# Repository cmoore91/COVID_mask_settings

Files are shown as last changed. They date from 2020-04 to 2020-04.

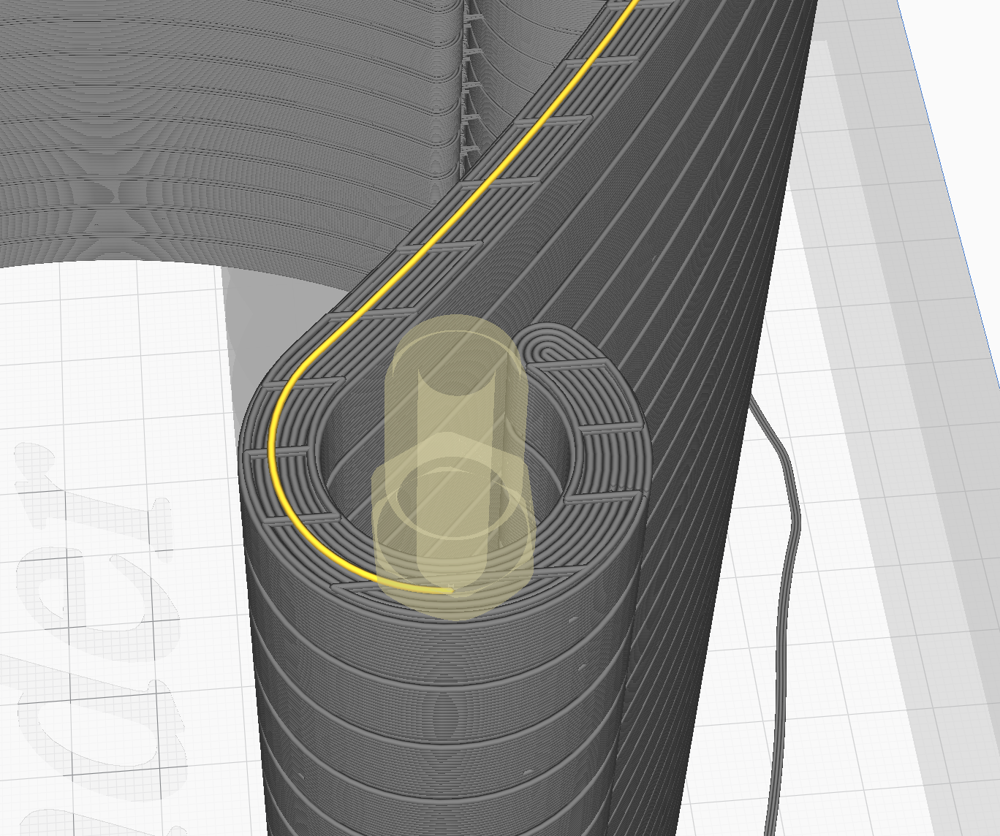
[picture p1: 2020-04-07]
inside_walls_first.png

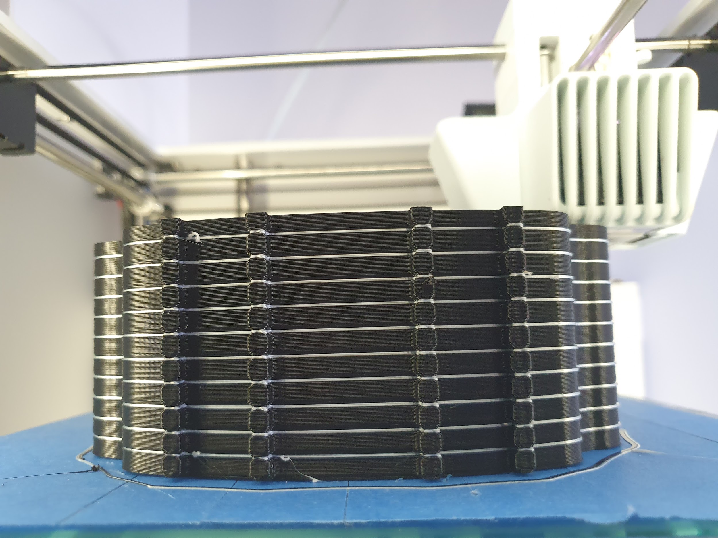
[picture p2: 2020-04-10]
protective-visor-by-3dverkstan/breakaway_stack3.jpg

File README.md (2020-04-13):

# COVID mask settings
### 3D print settings I have optimized for mass production of the 3DVerkstan faceshield on an Ender 3 Pro.  
### Disclaimer: This is intended to assist Chapman University affiliated personnel for charity purposes, and I am not liable for your printer imploding  

* Printer: Creality Ender 3 Pro with OctoPi and BLtouch self-leveling bed 0.4mm nozzle
* Slicer: Ultimaker Cura 4.5.0
* CAD Software: Autodesk Fusion360
* Filament: Matterhackers PRO PLA

In this repository, I have attached the STL and cura profile I used if you want to tweak the settings.  I have 2 versions: 
* fast and loose: decent quality for rapid speed.  some unsupported areas are a little rough
* slow and smooth: I recommend this one.  at 0.3mm layer height you can get it almost as fast as above.  

I also have 2 open source droplet containment box designs.
* the first one is mine: https://a360.co/2RrGePB  
* the second one is in the Flatpackv5 folder (from https://www.aerosolblock.org/)

Otherwise find the
plug-and-play g-code file here: https://drive.google.com/a/chapman.edu/file/d/1QBju7udUCOP3C-gHDJ0qYh54JztkdXBj/view?usp=sharing
* Note: if you dont have self-leveling, you need to remove the relevant g-code from the preamble in a text editor.

This can accomplish printing 35 Shield Frames in <30 hours, or 50 minutes per shield.  

The frames are easily cracked apart with a paint scraper, razor blade or metal spatula.  I recommend cracking apart the tips of the arms first.  

For people not using Cura slicer and want to copy the settings I used, but warning: mileage may vary.  

The **CRITICAL** slicer settings are as follows:
* Orientation: 90 degrees rotation from default (so mirror plane of the frame is parallel to x-axis) (yes this matters)
* Layer Height: 0.28 mm
* Wall Line Count: 5 
* Top Layers: 3
* Outer Before Inner Wall: NOOOOO
* Filter Out Tiny Gaps: Yes
* Fill Gaps Between Walls: No
* Infill Density: 5%
* Infill Pattern: Gyroid
* Connect Infill Lines: Yes
* Min Infill Area: 4 mm^2
* Print Temp: 210 C
* Build Plate Temp: 60 C
* Speed: 60 mm/s
* Support Placement: Everywhere
* Support Wall Line Count: 0
* Support Density: 10%
* Min Support Area: 10mm^2
* Build Plate Adhesion: Skirt
* IT IS VERY IMPORTANT YOU SET THE WALLS TO START FROM THE INSIDE FIRST AND MOVE OUTWARDS TO TAKE ADVANTAGE OF THE VERY SPARSE SUPPORTS

Here is the original design.  Make sure to use North American Version 
https://3dverkstan.se/protective-visor/protective-visor-versions/

contact me at c.stephen.moore@gmail.com with any feedback or questions

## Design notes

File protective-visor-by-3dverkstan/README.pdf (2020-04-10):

# Protective Visor by 3DVerkstan

### By: (erikcederb) License: Commercial use is allowed, you must attribute the creator, you may remix this

work and the remixed work should be made available under this license.

### Published on: Apr 03, 2020 Located at: http://www.youmagine.com/designs/protective-visor-by-3dverkstan Short description:

Protective visor optimized for fast FDM printing

### Description:

I would like to thank our fantastic team at 3DVerkstan who all have contributed massively! Since the medical community currently (2020-03-20) has a urgent need for protective visors and other PPE for our heroes that spends their days battling COVID-19, myself and my co-workers at 3DVerkstan have spent a lot of time during the past few days designing a printable visor. This in a WORK IN PROGRESS, and might get multiple revisions during the coming days/weeks, but this first released version is the first one on its way to be tried out by a local hospital. The plastic shield can be made out of any semi-stiff plastic sheet between 0.1 and 1mm, including overhead film, cover sheets for binding machines etc, as long as it is available in a suitable format. There currently are 3 different versions. One for SWEDEN, one for EUROPE and one for NORTH AMERICA. For information about the different versions: https://3dverkstan.se/protective-visor/protective-visor-versions/ If you need it to sit tighter on your head or if you are leaning over patients a lot and worry about it falling off, a simple rubber band can be put over the two hooks in the back. For help with print settings: https://3dverkstan.se/protective-visor/protective-visor-print-guide/ You need approx a 210x210mm build area to print two at a time, and about 160x190mm if you are OK with only doing one at a time. The 3MF file shows how you can put 3 of these on a single Ultimaker S5 print bed and print them in 21 minutes per piece with a 0.8 mm nozzle.

If you can, please use the online documentation found at http://www.youmagine.com/designs/protective-visorby-3dverkstan because those may have been been updated. Also, there you can interact and provide praise and/or feedback.

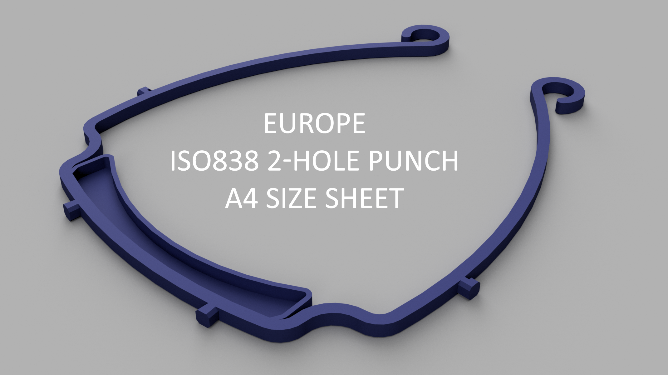
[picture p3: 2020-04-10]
protective-visor-by-3dverkstan/Visor_frame_ISO838_A6.png

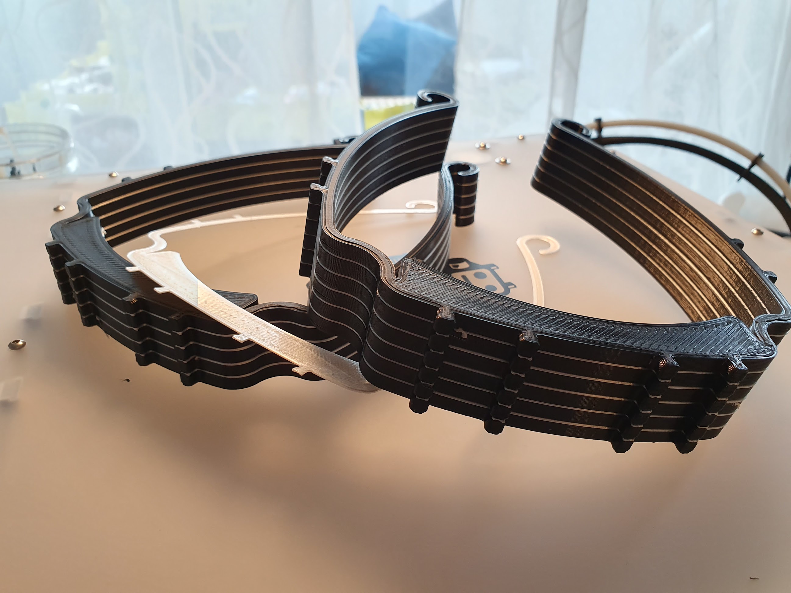
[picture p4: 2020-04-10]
protective-visor-by-3dverkstan/breakaway_stack1.jpg

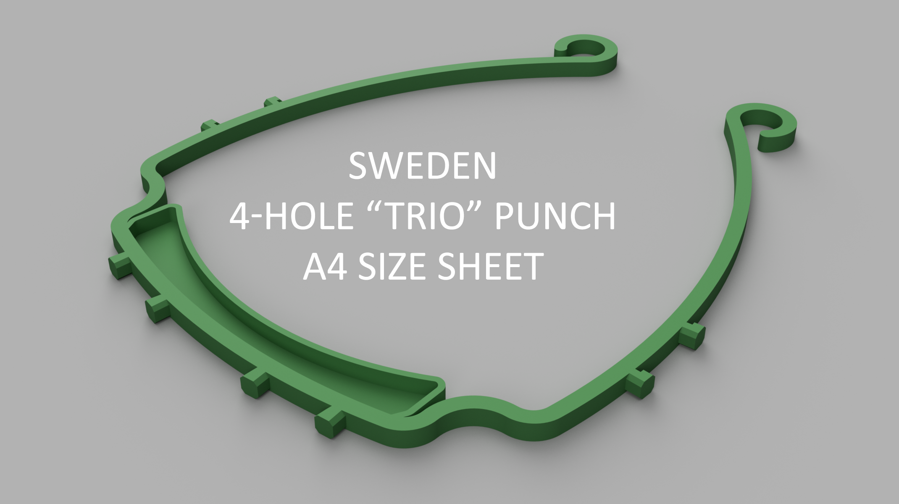
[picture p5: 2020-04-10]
protective-visor-by-3dverkstan/Visor_frame_SWEDEN_A6.png

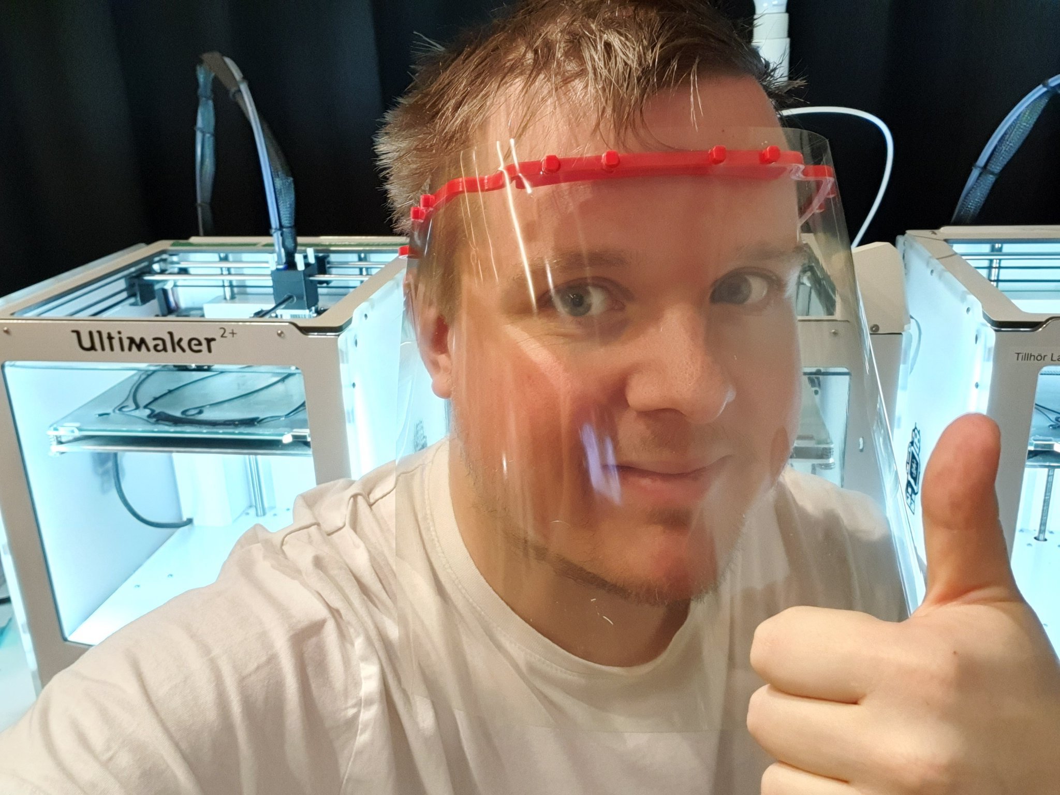
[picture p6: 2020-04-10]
protective-visor-by-3dverkstan/ErikC.jpg

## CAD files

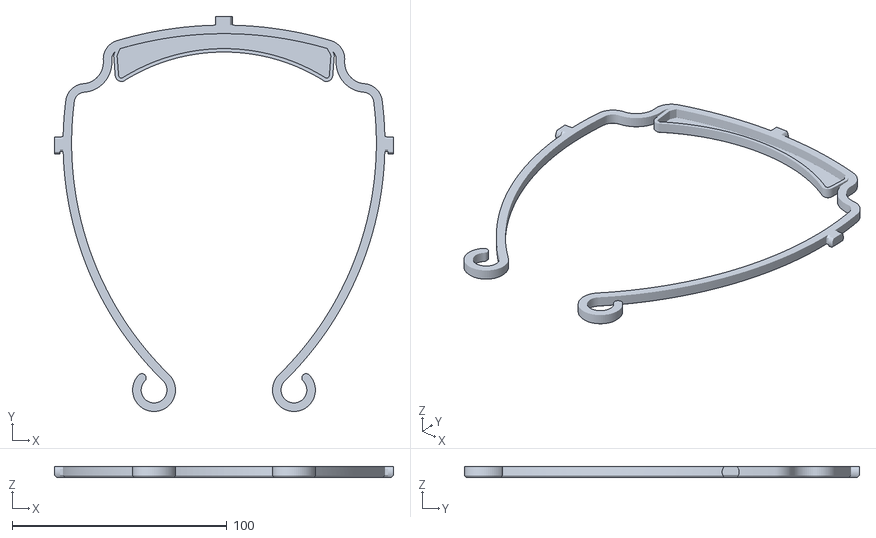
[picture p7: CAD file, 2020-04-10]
fast and loose/Visor_Frame_NORTH_AMERICA_LETTER_v2.stl
158.1 x 184.1 x 5.00

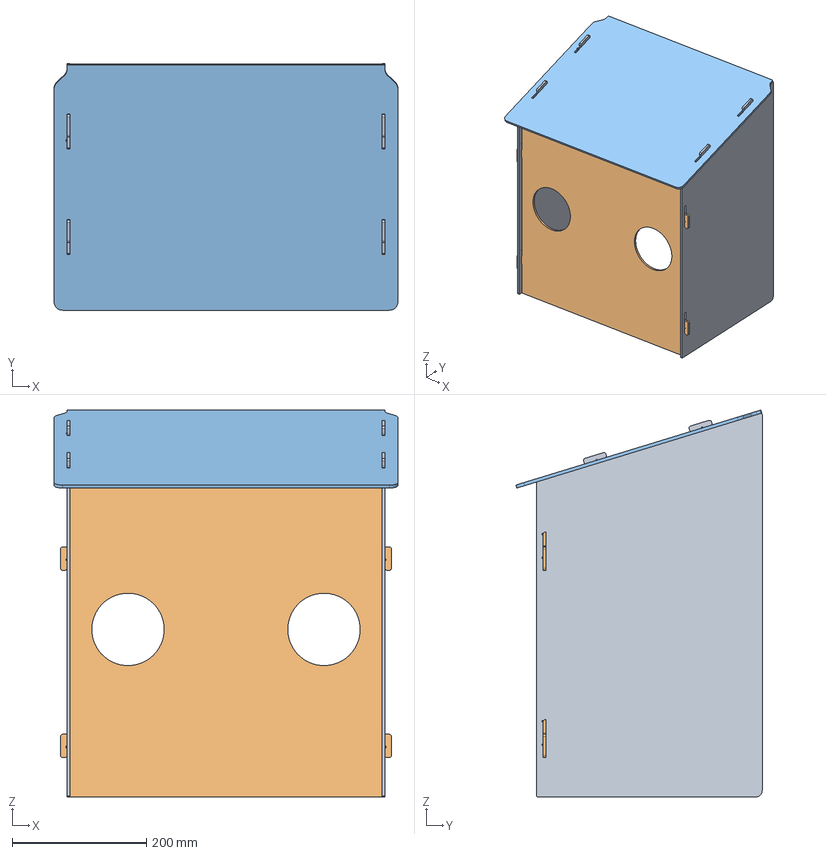
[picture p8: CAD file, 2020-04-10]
FlatPackV5/FlatPackV5/Polycarbinate Box - Flatpack - V5 v38.step
512.7 x 367.7 x 577.3 mm
Left Side
Right Side
Front
Top

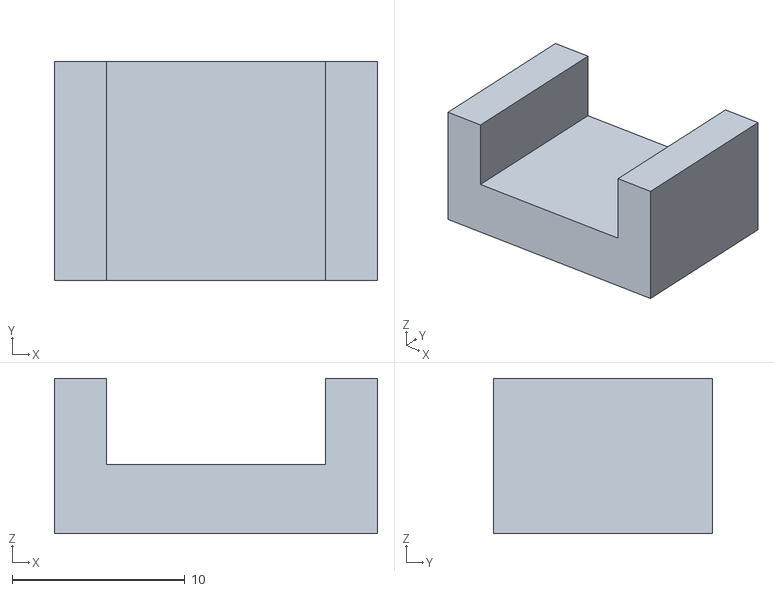
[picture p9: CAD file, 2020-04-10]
protective-visor-by-3dverkstan/Letter-spacer-6hole.stl
18.7 x 12.7 x 9.00

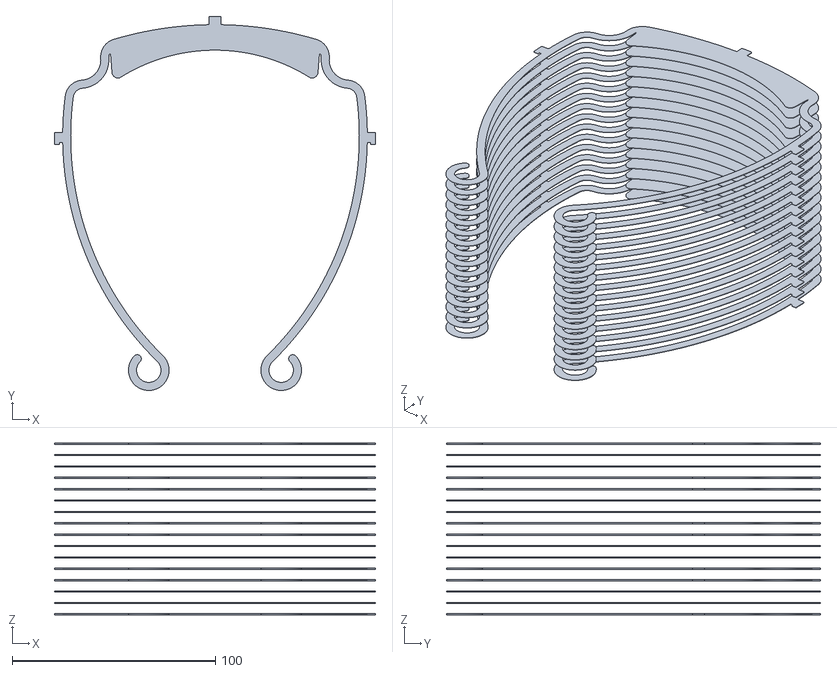
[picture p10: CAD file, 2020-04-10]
protective-visor-by-3dverkstan/NORTH_AMERICA_3-hole_v4_stacked_for_dual_extrusion/Visor_Frame_NORTH_AMERICA_letter_3-hole_v4-solid_front-support_stack_17pcs_95mm.stl
158.1 x 184.1 x 84.6

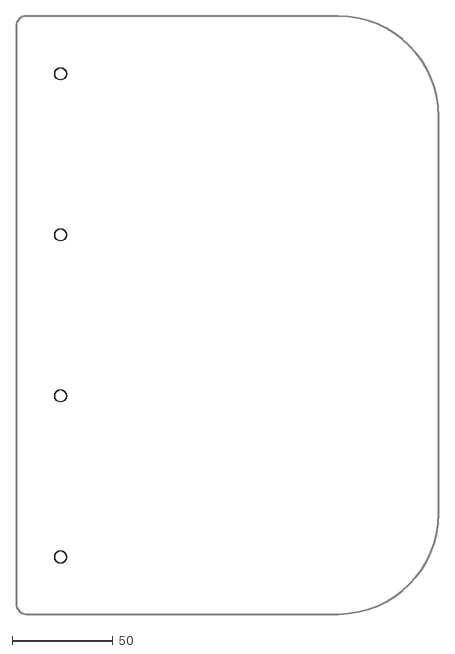
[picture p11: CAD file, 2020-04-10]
protective-visor-by-3dverkstan/Lasercut-shield-EUROPE-4hole.dxf
210.0 x 297.0

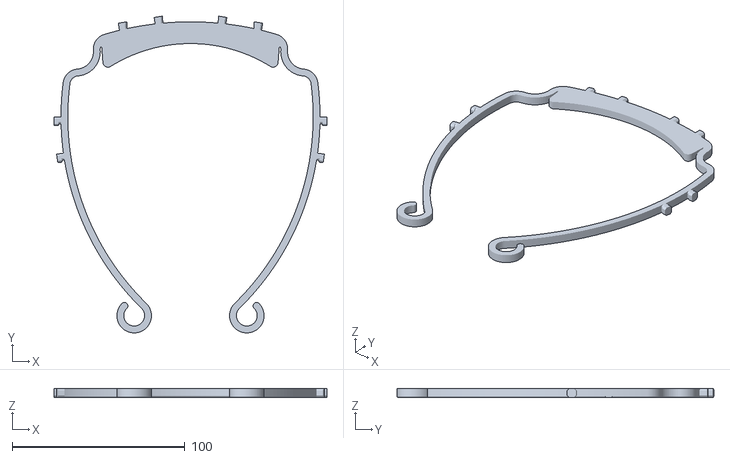
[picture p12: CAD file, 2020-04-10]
protective-visor-by-3dverkstan/Visor_Frame_SWEDEN_V11-solid_front.stl
158.0 x 183.4 x 5.00

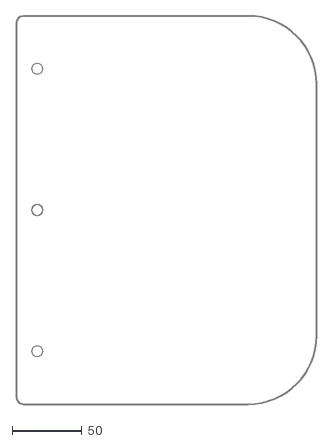
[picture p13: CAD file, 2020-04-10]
protective-visor-by-3dverkstan/Lasercut-shield-NORTH-AMERICA-3-hole-letter-format.dxf
216.0 x 279.0

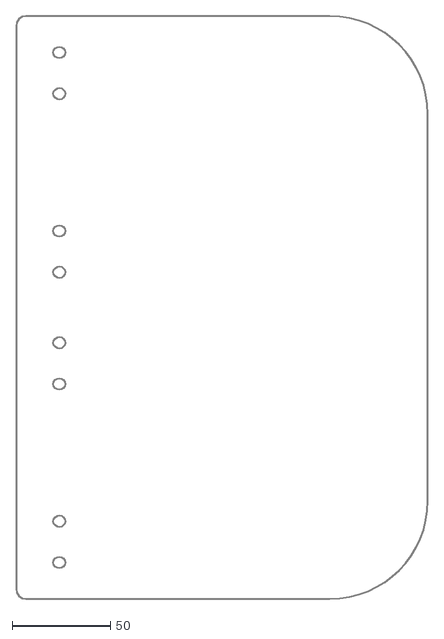
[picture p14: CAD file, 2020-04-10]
protective-visor-by-3dverkstan/Lasercut-shield-SWEDEN-A4.dxf
210.0 x 297.0

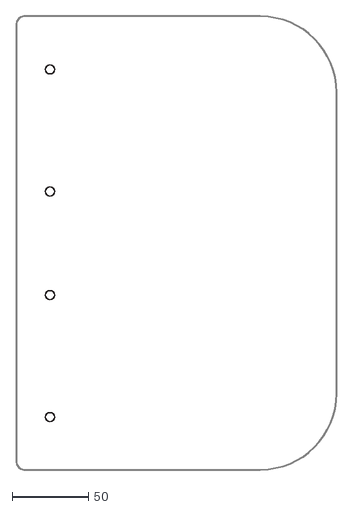
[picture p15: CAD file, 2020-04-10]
protective-visor-by-3dverkstan/Lasercut-shield-EUROPE-ISO838-A6.dxf
210.0 x 297.0

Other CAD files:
protective-visor-by-3dverkstan/Visor_frame_EUROPE_80mm_4hole_v2.stl
protective-visor-by-3dverkstan/Visor_Frame_NORTH_AMERICA_letter_6-hole_v5-1mm_front.stl
protective-visor-by-3dverkstan/Visor_Frame_NORTH_AMERICA_letter_3-hole_v4-solid_front.stl
protective-visor-by-3dverkstan/Visor_Frame_NORTH_AMERICA_letter_3-hole_v4.stl
protective-visor-by-3dverkstan/Visor_Frame_NORTH_AMERICA_letter_6-hole_v5.stl
protective-visor-by-3dverkstan/Visor_Frame_NORTH_AMERICA_letter_6-hole_v5-solid_front.stl
protective-visor-by-3dverkstan/Visor_Frame_NORTH_AMERICA_letter_3-hole_v4-1mm_front.stl
protective-visor-by-3dverkstan/Visor_frame_EUROPE_80mm_4hole_v2-solid_front.stl
FlatPackV5/FlatPackV5/Polycarbinate Box - Flatpack - V5 v38.f3d
droplet box/corner reinforced box v6.f3d
protective-visor-by-3dverkstan/Lasercut-shield-NORTH-AMERICA-6-hole-letter-format.dxf
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

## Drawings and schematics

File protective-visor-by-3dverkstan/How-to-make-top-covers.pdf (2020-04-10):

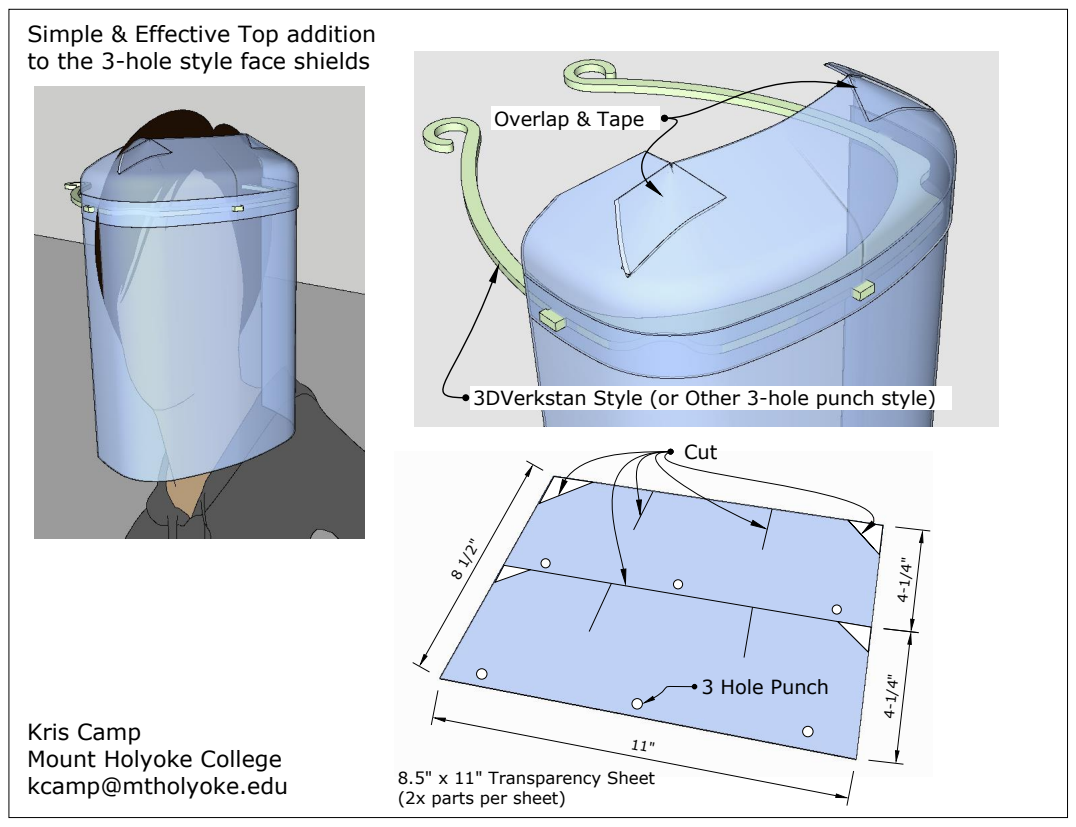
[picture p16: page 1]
Overlap & Tape; 3 Hole Punch

Simple & Effective Top addition
to the 3-hole style face shields

3DVerkstan Style (or Other 3-hole punch style)

Kris Camp
Mount Holyoke College
kcamp@mtholyoke.edu

8.5" x 11" Transparency Sheet
(2x parts per sheet)

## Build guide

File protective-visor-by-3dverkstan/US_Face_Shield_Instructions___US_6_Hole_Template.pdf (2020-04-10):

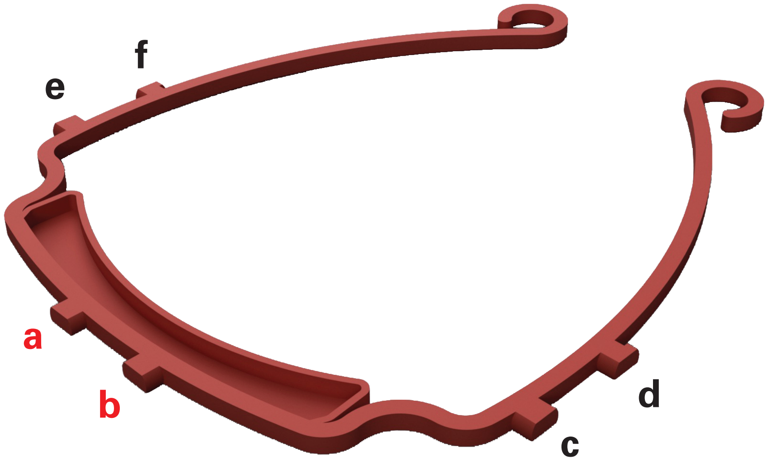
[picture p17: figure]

Attach the 6-hole clear plastic shield (1) to the plastic head band (2): first push the two center holes a and b of the clear plastic shield into buttons a and b of the plastic head band. Once a and b holes are in place wrap the clear plastic shield carefully around the frame of the plastic head band and insert into side buttons c and d being careful not to rip the plastic when putting it on button d which has a slight hook feature to hold it in place. Then repeat for side buttons e and f.

MATERIALS
1. 3 Hole "Letter" size punch.
2. US Letter (8.5” x 11”) clear plastic acetate (~0.2mm PET recommended).
3. Template: see back of this instruction sheet for template or go to https://www.youmagine.com/designs/protective-visor-by-3dverkstan to download PDF: Laser-cut Shield North America 6 Hole Letter Format.
4. Scissors.

HOW TO DO THE PUNCHING
1. Set your hole punch to the setting for a Letter sheet.
2. Set or make a 1/2" spacer to create a 6-hole pattern with a 1" offset on your hole punch. The 1/2" spacer is what creates the hole offset needed. Figure A shows 1/2" spacer shown in red.
3. Make one punch along one of the long sides, with the short edge resting and aligned with your spacer piece.
4. Flip the clear plastic sheet, and make one punch on the opposite side, so you end up with 6 holes along the same edge.
5. Use scissors to trim bottom corners as shown in the Diagram 1-1.

# Protective Visor by 3DVerkstan

Published on Mar 26, 2020, By erikcederb.

### License: Commercial use is allowed, you must attribute the creator, you may remix this work and the remixed work should be

made available under this license.
http://www.youmagine.com/designs/26808 | Hosted on

# PACKAGE CONTENTS

1. 6-hole clear plastic shield
US letter size (8.5” x 11”)

### 2. Plastic head band 3. Instruction sheet and 6-hole shield

template printed in the back of this instruction sheet

# ASSEMBLY INSTRUCTIONS

# TO MAKE ADDITIONAL 6-HOLE CLEAR PLASTIC SHIELDS (8.5” X 11”)

1 2

e f | a b | c d

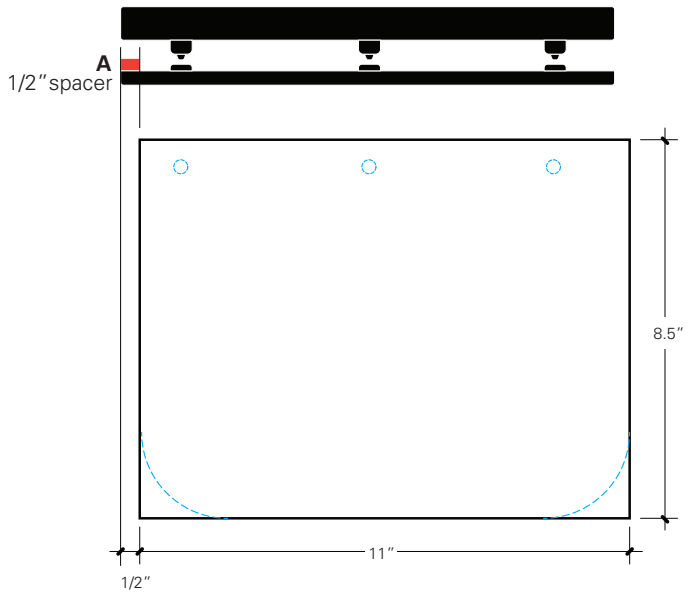
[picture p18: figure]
A 1/2”spacer

Diagram 1-1 showing how to align the US Letter clear plastic sheet with the hole punch to obtain the correct position for the first three holes, shown in blue.
See back for 6-hole shield template.

INSTRUCTION SHEET DESIGNED BY SYLVIA CEDEÑO - WWW.POGODESIGN.US

## 6-HOLE SHIELD TEMPLATE - US LETTER (8.5” X 11”)

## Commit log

2020-04-10 Updated with folders of different versions
    updated with a slightly slower yet higher quality frame, and I am also switching to 6 holes since people have been saying they are better.
    I also added design files for an aerosolization containment box from https://www.somethinglabs.org/intubation-box
    [Lasercut-shield-EUROPE-4hole.dxf, Lasercut-shield-EUROPE-ISO838-A6.dxf, Lasercut-shield-NORTH-AMERICA-3-hole-letter-format.dxf, Lasercut-shield-NORTH-AMERICA-6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]
2020-04-11 Create corner reinforced box v6.f3d
    [corner reinforced box v6.f3d]
